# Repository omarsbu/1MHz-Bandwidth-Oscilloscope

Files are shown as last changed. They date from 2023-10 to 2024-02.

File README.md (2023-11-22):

# 1MHz-Bandwidth Mixed Signal Oscilloscope

- Created a cohesive mixed signal oscilloscope system integrating both hardware and software components.

- Designed a 50-ohm, 1MHz bandwidth analog front end with versatile signal processing capabilities
including, AC/DC coupled inputs, single-ended to differential signal conversion, SPI controlled variable gain
and attenuation, precise DC offset biasing, a 2nd order active anti-aliasing filter, and precise analog trigger
circuitry to interface with an 10 MSPS ADC.

- Developed Arduino C++ code for an ESP32 microcontroller to control an ILI9341 LCD display, enabling
real-time waveform plotting, XY cursors, frequency, period, duty cycle, and RMS measurements.
Implemented user-friendly controls via potentiometers and push buttons for vertical and horizontal scaling,
trigger level adjustment, and DC offset. Applied signal processing techniques for signal amplification,
attenuation, and dynamic upsampling and downsampling.

- A USB port outputs 5V of power so that an external microcontroller can be connected. The ADC output can also be read
  by an external microcontroller or FPGA. Header connectors can be used to read data from the analog front end and send
  control siignals to control signal conditioning.

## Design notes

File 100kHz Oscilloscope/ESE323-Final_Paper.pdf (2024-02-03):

Omar Mohamed

SBU ID - 113907357

ESE 323 – Modern Circuit Board Design and Prototyping

Final Paper

100KHz Bandwidth Oscilloscope

The goal of my project was to create a 100KHz bandwidth oscilloscope with control knobs for vertical

and horizontal scaling, dc offset addition/subtraction, trigger level adjustment, and XY measurement

cursors. I used Arduino IDE to write software in C++ for an ESP32 to plot the samples from the ADC on a

240x320 pixel TFT display, poll the control knobs, and perform tasks related to peripheral ICs. I designed

an analog front end for signal conditioning to maximize the ADC’s input range and triggering to plot a

stable waveform on an LCD display module. My goal is for oscilloscope to operate on a single +3.3V

power supply and be capable of receiving power from a USB connector or an AC adaptor. A block

diagram of my design is shown below:

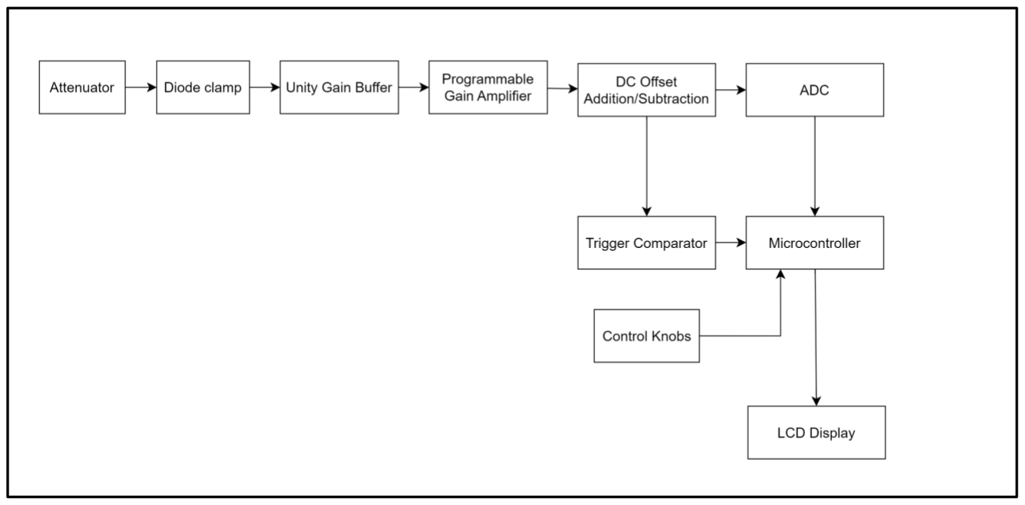
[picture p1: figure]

Circuit Description

Shown below is a schematic diagram of the input stage which consists of a pair of banana

connectors to connect external probes, a compensated L-pad attenuator with 1MΩ input

impedance, a diode clamp, and a unity gain buffer. A programmable gain amplifier is used as a

preamp to adjust the resolution and range of the analog-to-digital converter.

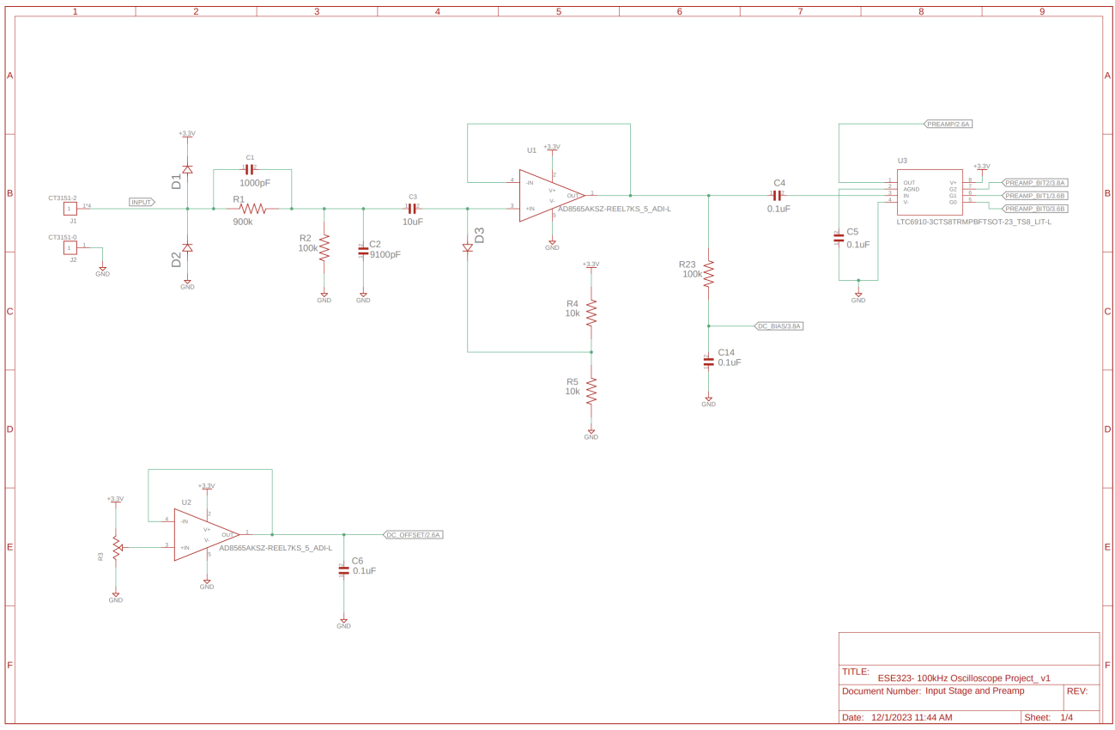
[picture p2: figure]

The Schottky diodes D1 and D2 are protection diodes which will forward bias and steer the flow of

current into the power supply if the input voltage is above or below the power supply rails.

Capacitors C1 and C2 are connected in parallel with resistors R1 and R2 to form a 10:1 L-pad attenuator.

The attenuator works in conjunction with the diode clamp to ensure that the input signal fits well within

the power supply rails so that signal distortion does not occur. If the input to the unity gain buffer is

outside of the range of the power-supply rails, then the signal will be clipped and there will be no way of

getting it to the ADC so it can be digitized. The positive clamp is used to shift the input signal up by the mid-supply voltage. This allows for negative input voltages to be measured with a single positive power

supply because it will automatically bias the input signal near the mid-supply voltage. The attenuator

helps to ensure that the input signal is small compared to the clamp voltage which increases the

likelihood of the input voltage level always being near the mid-supply voltage.

The trade-off of the clamp is that positive voltages above the mid-supply voltage will be shifted above

+3.3V and will be clipped while negative voltages above -1.65V will be shifted to within the single-supply

range. This is a good trade off to make since it allows for my oscilloscope to measure bipolar signals

which are of greater interest than signals with a single polarity. The positive input range can always be

increased by adding more attenuation to the input stage so there is less chance of being clipped.

The screenshot shown below is taken from an LTspice simulation of the analog front end:

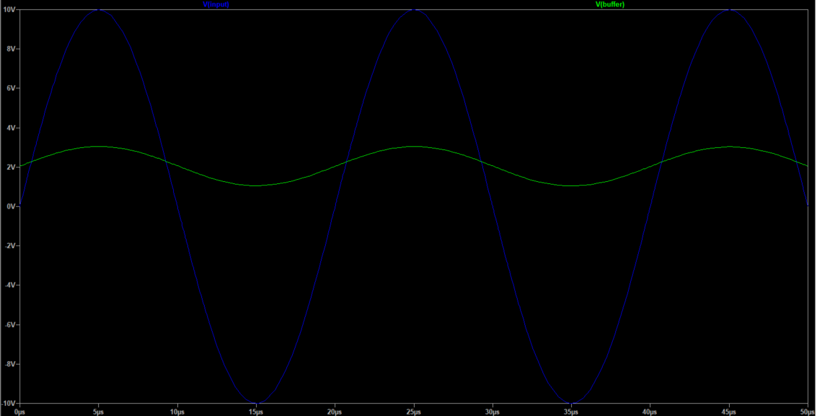
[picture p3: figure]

A 10V amplitude sine wave with 0 dc bias is applied at the input. The signal is attenuated and shifted up

to within the supply range of the op amp buffer so that even large negative voltages can still be

accommodated with a single positive power supply. Upon inspection, I forgot to account for the forward

voltage across the diode when clamping so the signal is shifted above the value I would like, however,

the values of resistors R4 and R5 can be adjusted to achieve a different clamp voltage.

Connecting capacitors C1 and C2 in parallel with resistor R1 and R2 provides compensation for the diode

clamp capacitance as well as the input capacitance of the amplifier and any stray capacitance or

inductance present in the resistors or circuit board. This compensation scheme employs pole-zero

cancellation to suppress undesirable frequency dependence caused by the additional reactance. If the

resistor and capacitor values are chosen so that the pole and the zero are superimposed, the transfer

function of the attenuator becomes independent of frequency. The component values are selected so

that the following relationship is satisfied:

R1C1 ≅ R2C2

The screenshot shown below is taken from an LTspice simulation of the attenuator output without compensation. The simulation shows that the desired 10:1 attenuation factor cannot be achieved without additional compensation.

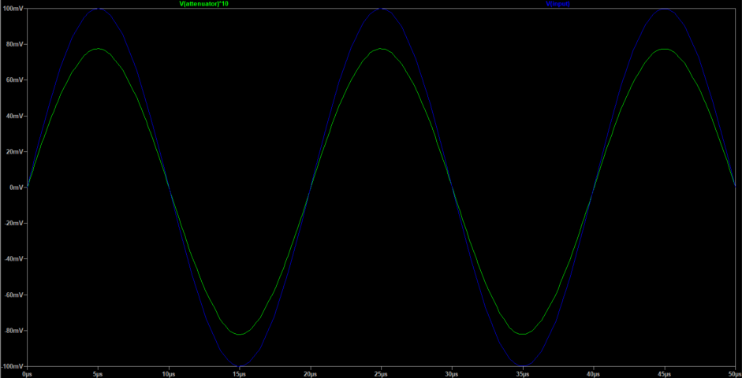
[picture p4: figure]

The screenshot shown below is taken from an LTspice simulation of the attenuator output with the appropriate compensation, the output is much closer to the desired 10:1 attenuation factor. The simulation results show that the attenuator performance is greatly improved by compensation.

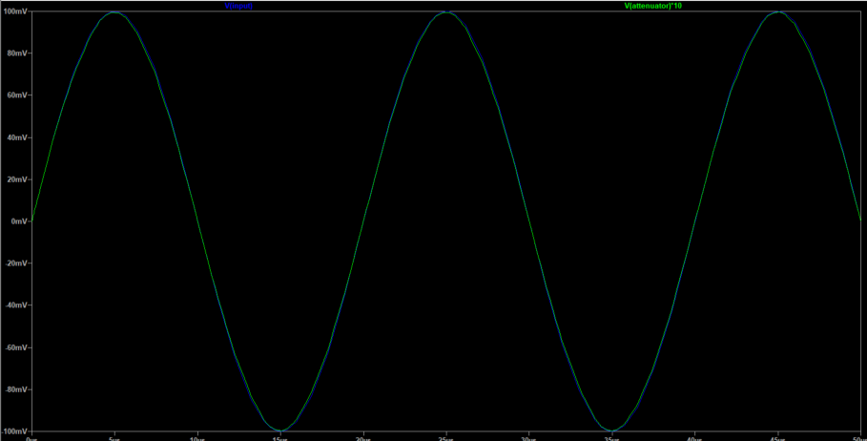
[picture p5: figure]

The programmable gain amplifier is used to provide variable amplification to the input signal so it can be

scaled to the ADC’s full range for maximum resolution. The gain of the amplifier is determined by the

volts per division setting on the oscilloscope. A lower volts per division setting would correspond to a

higher gain so that smaller signals can be scaled to the full range of the ADC and a higher volts per

division setting would correspond to a lower gain so that larger signals can still fit within the input range

of the ADC.

The LTC6910-2 is a 3-bit programmable gain amplifier with gain steps of 6dB (powers of 2). The gain of

the amplifier is cascaded with the attenuator so that variable gain and attenuation can be achieved. If

the gain of the amplifier is lower than the attenuation factor, then there will be a net attenuation of the

input and if the gain of the amplifier is higher than the attenuation factor then there will be a net

amplification of the input signal. The volts per division setting of the oscilloscope is implemented by

cascading the attenuator and PGA so the dynamic range of the ADC can be adjusted for more or less

effective resolution depending on the information being displayed on the screen.

The input signal is ac coupled to the amplifier so that only the ac portion of the signal is amplified.

Amplifying the dc component is of little use if it is larger than a few LSBs since it will mainly just shift the

input signal closer to the supply rails and introduce distortion or clipping. The signal is dc coupled to the

ADC of the ESP32 by measuring the voltage across a capacitor with a large RC time constant. If the time

constant of the capacitor is very large, then a low pass filter is formed to only allow dc to pass through.

The dc component of the input signal can then be measured with the ESP32’s ADC which is noisier and

has a lower sample rate than the external ADC being used. The noise and sample rate are less important

for the dc component than the ac component since it is just a vertical displacement of the ac component

on the display. An averaging filter can be implemented in software to remove any noise on the dc

measurement from the ESP32’s ADC.

DC offset addition or subtraction is implemented through the use of summing and differential op amp

configurations. The ADG1419 is a SPDT switch IC which is used to select between the outputs of the two

op amps. The dc offset select signal is a digital signal which is read from a push-button and set or cleared

by the microcontroller so that a dc offset can be added or subtracted from the amplified signal. The

output from the switch is connected to a comparator which compares the signal to the trigger level and

outputs a rising or falling edge when the signal passes through the trigger level. This edge triggers an

interrupt on the microcontroller which causes the waveform to be plotted on the screen. Since the

waveform is only plotted when the signal passes through the trigger level, a stable waveform can be

displayed on the screen.

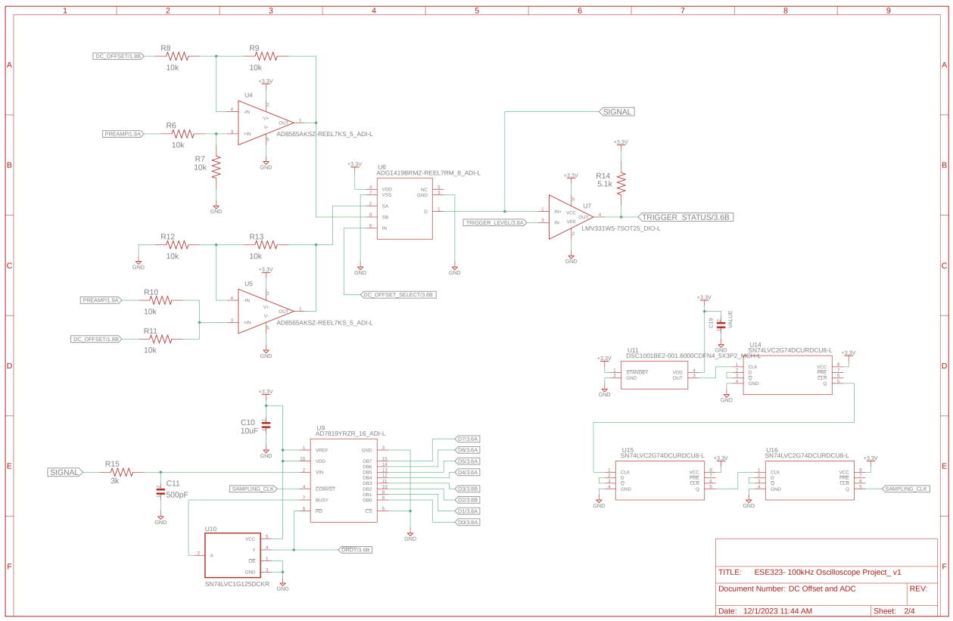
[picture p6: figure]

In hindsight, I now realize that the use of op amps for dc offsetting is a flaw in my design. The purpose of

dc offsetting is so that signals outside of the ADC’s input range can be shifted up or down to fit within the

appropriate input range. Since the reference voltage of the ADC is +3.3V which is the same as the power

supply voltage, using op amps for dc offsets does not do anything that cannot easily be done in software.

The op amps can only output voltages within its power supply rails which is no different from the ADC’s

input range, therefore, using op amps to shift the signal up or down does not provide any further

resolution to the ADC since the signal is already within its input range. Furthermore, the attenuator and

diode clamp at the input stage already perform the task of ensuring that the input signal is within the

ADC’s input range. Since the summing and differential op amps only serve to shift the signal up or down

within the ADC’s input range, they can be removed from the design and the same dc offsetting can be

implemented in software after the signal has been digitized.

The AD7819 is an 8-bit 200ksps SAR ADC, so a simple single-pole RC anti-aliasing filter is chosen with a

cutoff frequency close to the Nyquist-rate of 100kHz. A higher-order filter can be used to achieve a

steeper transition from the passband to stopband, however, this would require more components and

digital processing to flatten the passband response. I wanted to keep the design simple so that I could

finish as soon as possible. The RC-filter serves the purpose of preventing aliasing by filtering out

frequencies above the oscilloscope’s bandwidth, however, it also serves as a charge-bucket to reduce the

kickback settling time of the SAR ADC in between the conversion and acquisition phases by dumping

charge into the internal sample and hold circuit at the start of the acquisition phase.

The shortest possible time per division setting is proportional to the fastest sampling period (5

microseconds) multiplied by the number of samples displayed. In order to increase the time per division

setting on the display, a larger number of samples must be collected and then the sequence must be

decimated in order to display a waveform corresponding to the time per division setting. The ESP32 has

320KB of memory storage so there is enough memory to store a large number of 8-bit samples. The

sampling rate can be lowered to spread the samples over a longer time frame, however, this would

lower the oscilloscope’s bandwidth because I would have to ensure that the sampling rate was always

above the Nyquist rate.

A 200KHz sampling clock for the “conversion start” pin of the ADC is generated by using a 1.6MHz

oscillator and a D-flip-flop based frequency divider. Each stage divides the frequency by two, so three

flip-flops are cascaded to divide the frequency by eight and convert a 1.6MHz clock into a 200KHz clock.

A non-inverting buffer is used to increase the fanout of the BUSY pin as it must drive two input pins.

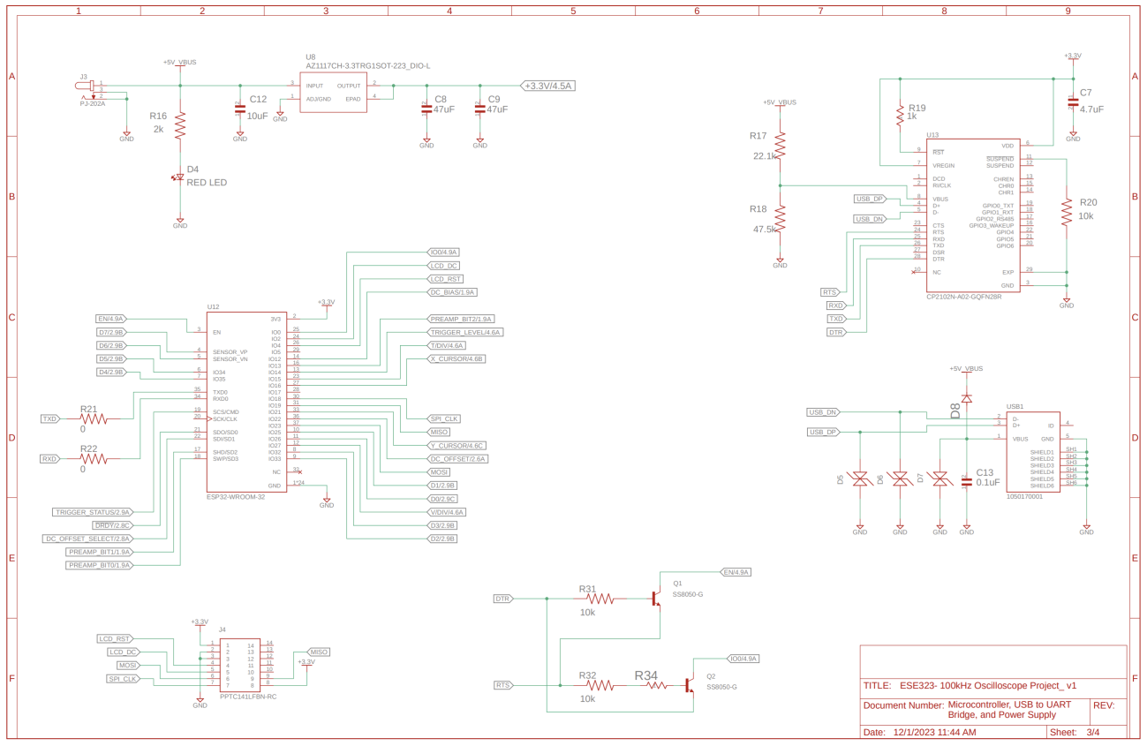
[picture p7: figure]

I have verified that I can sample all the GPIO pins connected to the ADC at a rate of 500kHz which is

more than twice the 200KHz frequency of the output from the ADC, therefore, no external FIFO buffer is

required to lower ADC’s output data rate. The microcontroller will poll the ADC output and store the

samples in memory and then plot the waveform on an LCD display after receiving the edge-triggered

interrupt from the trigger comparator.

A USB to UART bridge is used to program the microcontroller using Arduino IDE and a simple LDO

regulator is used to achieve the +3.3V power supply from a USB connector or a +5V ac adaptor. A red LED lights up when the power supply is connected to indicate that the board is receiving power. The ac

adaptor output and USB connector power pin are connected to the same node, however, a Schottky

diode is placed at the VBUS pin of the USB connector to prevent any current from flowing into the USB

host device. A 14-pin female header connector is used to mount an ILI9431 2.8” TFT LCD display on the

board.

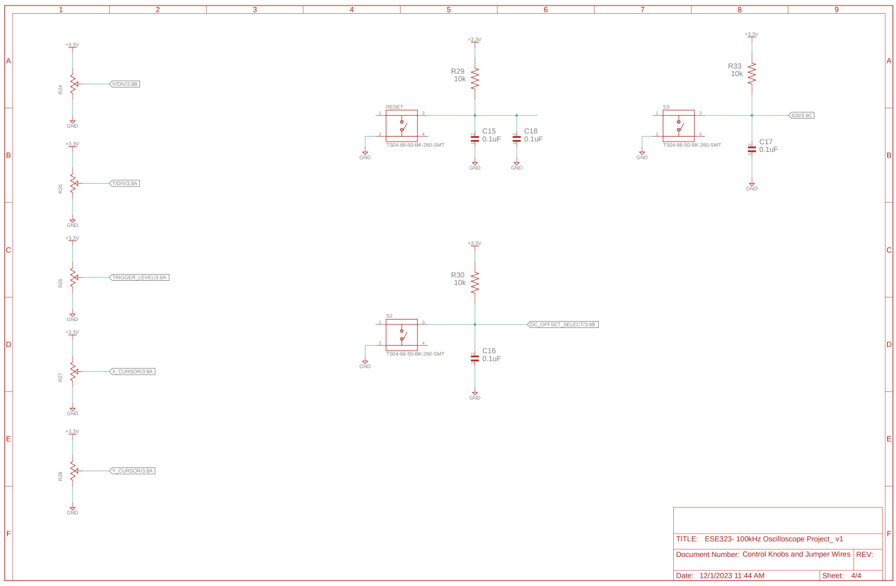
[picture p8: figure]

The control knobs are implemented using potentiometers. The output from the potentiometers

corresponding to the volts per division, time per division, and XY cursor settings are read by the ESP32’s

ADC and then software is used to map the analog values from the potentiometers onto the appropriate

horizontal/vertical scaling values and cursor positions on the screen. The PGA bits are chosen so

maximize resolution for a given volts per division setting and sample decimation is determined from the

time per division setting. The outputs from the trigger level and dc offset potentiometers are connected

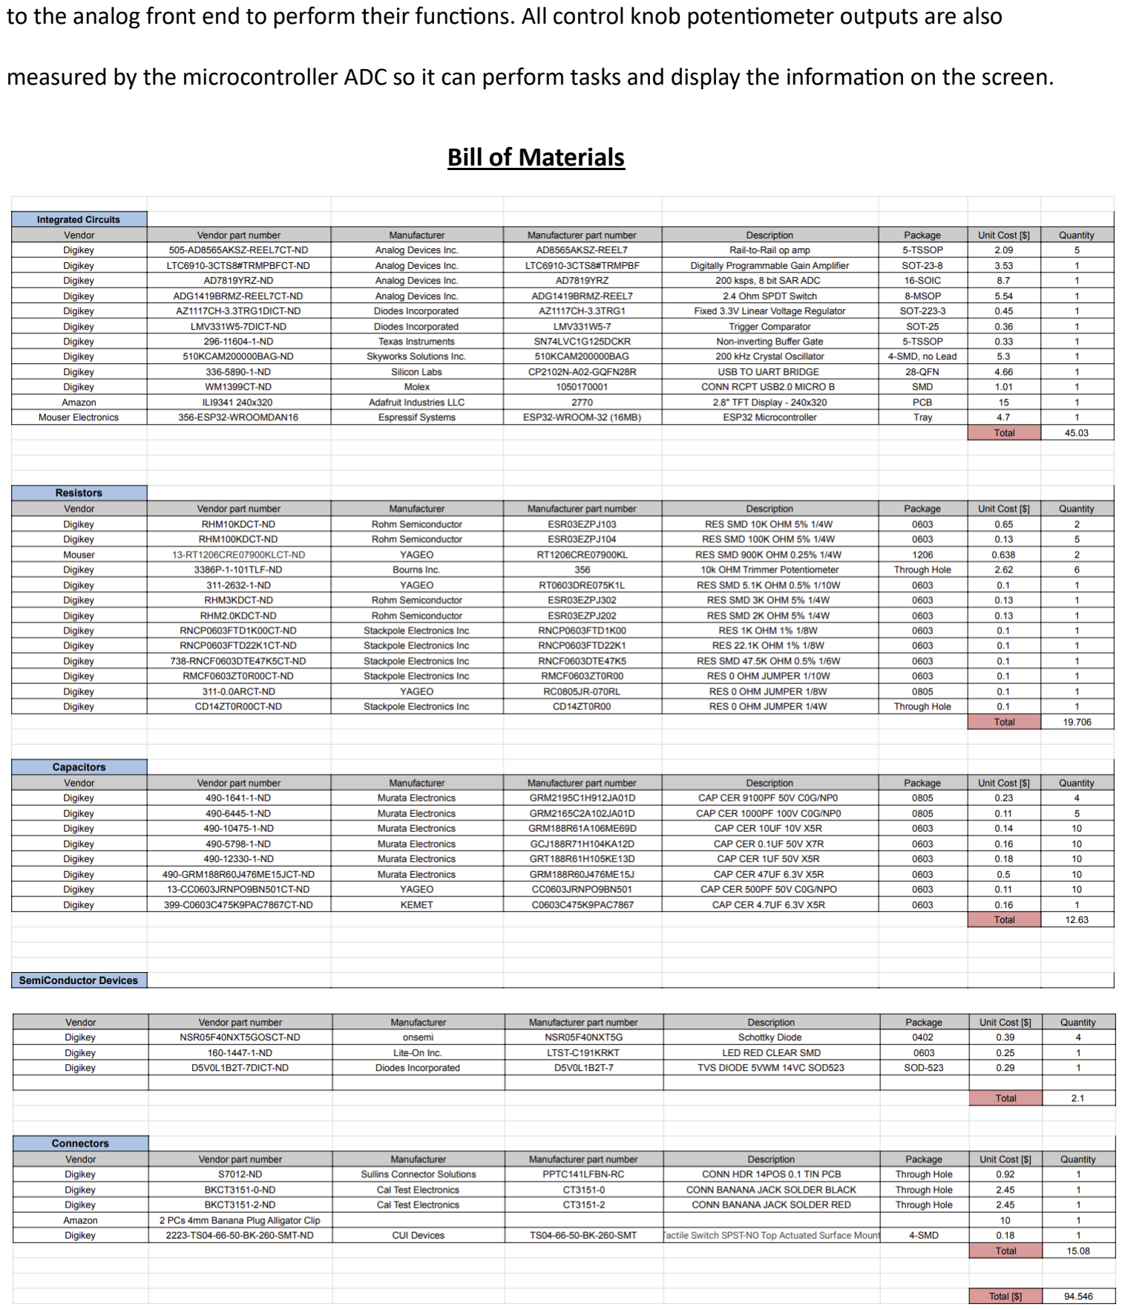
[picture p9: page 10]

to the analog front end to perform their functions. All control knob potentiometer outputs are also

measured by the microcontroller ADC so it can perform tasks and display the information on the screen.

Bill of Materials

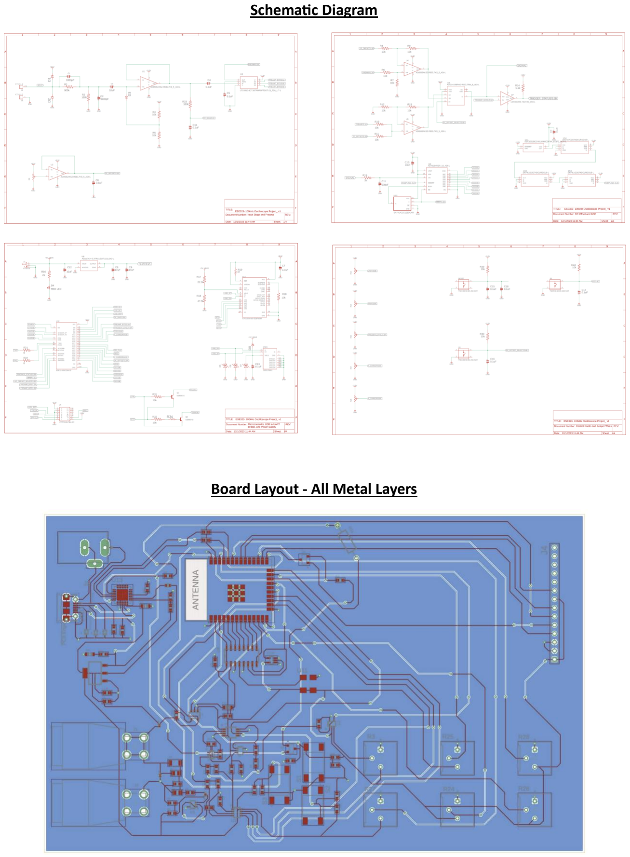
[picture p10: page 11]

Schematic Diagram

Board Layout - All Metal Layers

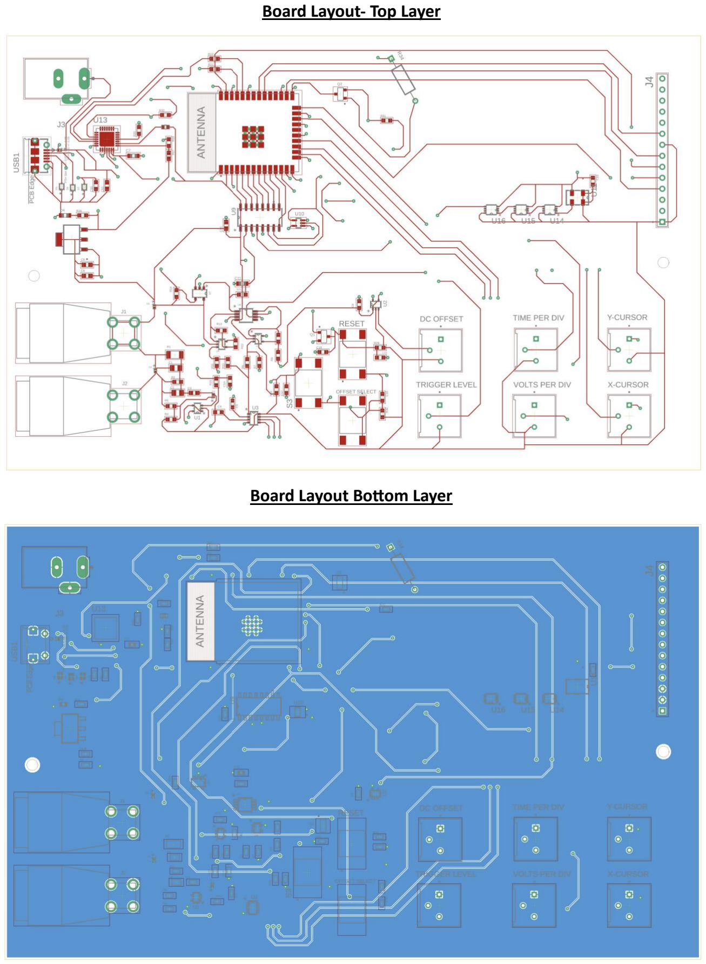
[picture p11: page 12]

Board Layout- Top Layer

Board Layout Bottom Layer

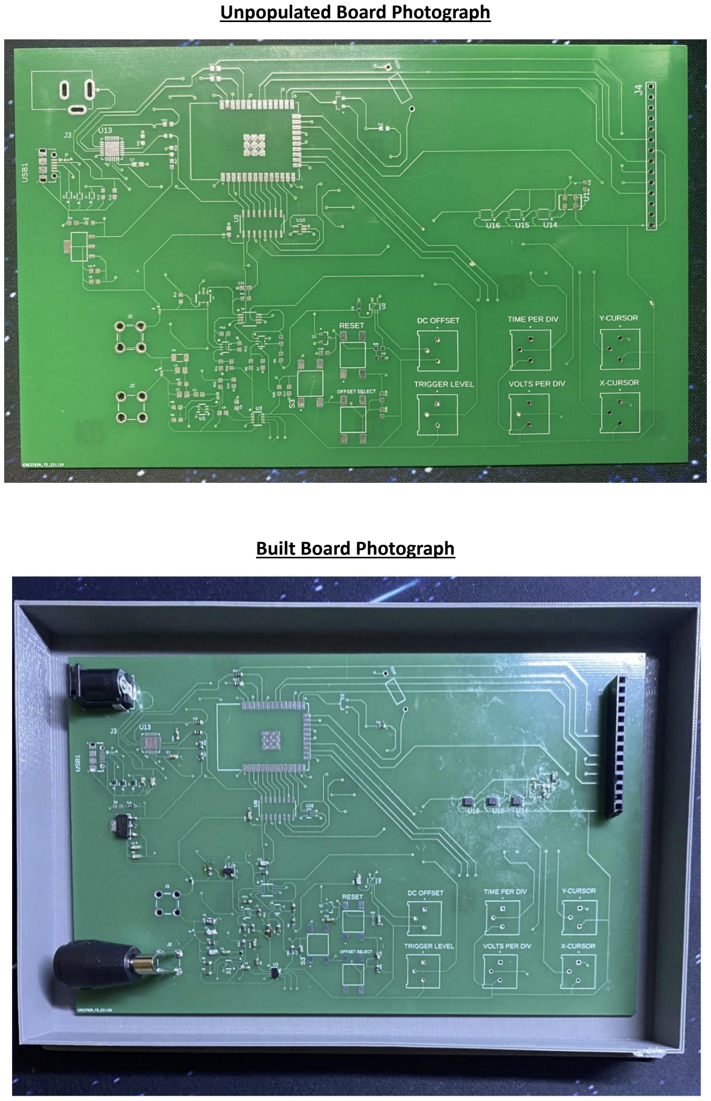
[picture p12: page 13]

Unpopulated Board Photograph

Built Board Photograph

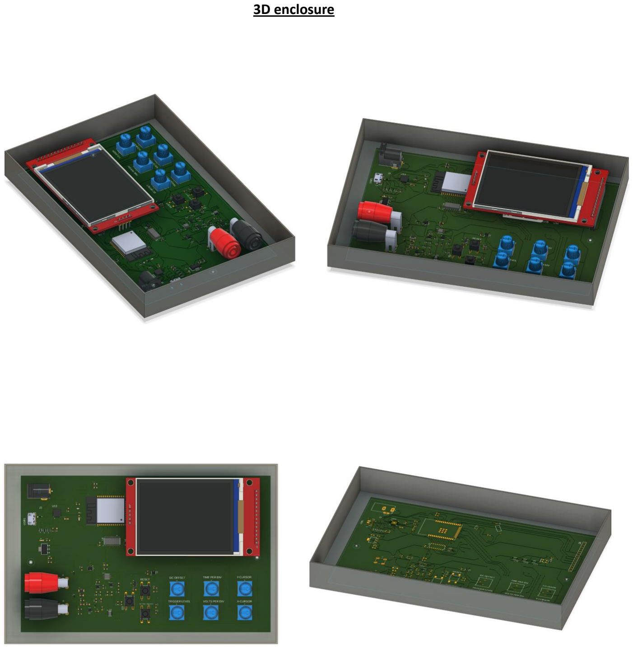
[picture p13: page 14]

3D enclosure

Software

This is a demonstration of the display code that I wrote for my project. I wanted to include a

photo of the code running on the actual display that I bought, however, I believe that I may have

left it in the lab over the weekend because I could not find it in my room. So instead, I used an

online Arduino simulator called Wokwi to simulate the code and I took a screenshot of the

results. The frequency , duty cycle, and period measurements are just arbitrary values that I

hardcoded onto the display. I tested the XY-cursors, volts per div, and time per div functions out

with my keyboard and the code worked how I wanted it to.

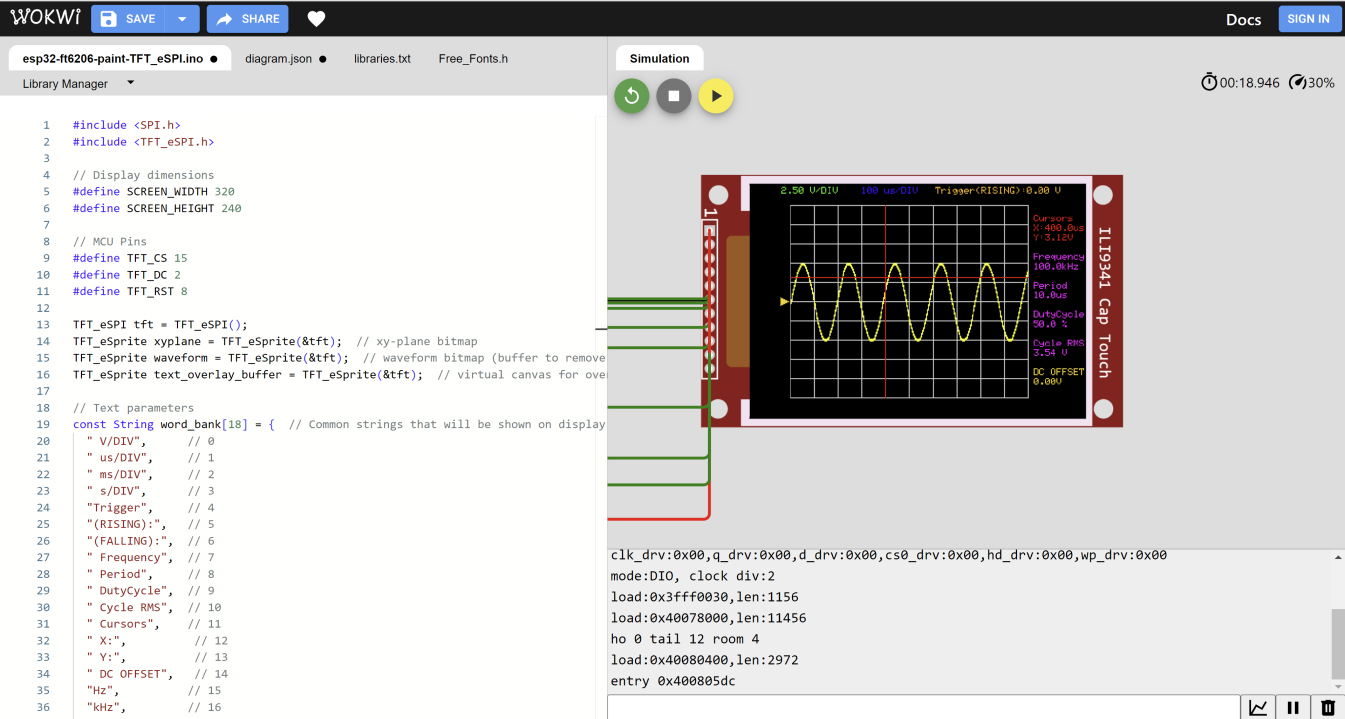
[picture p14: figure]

Results

My original design was too complicated to finish by the end of the semester, so I had to completely

redesign it from scratch over thanksgiving break. I was able to finish the layout and schematic,

unfortunately, I was not able to finish assembling my board. I lost most of my op amps and blew off

some of the pads for the board that I had made the most progress on. Also, the microcontroller that I

ordered from Digikey did not match the footprint that I found online so I could not solder it onto the

board. I decided not to solder on some of the more expensive components so I could save them for later.

I am going to order a new microcontroller that fits on the pad on my board, and I am also going to get

replacements for the components that I lost so I can try to assemble it next semester. I did get a chance

to test the programmable gain amplifier by soldering some of the gain bit pins to +3.3V. The two images

shown below are screenshots from one of the oscilloscopes in the lab. The green waveform (channel 2)

is the input signal, and the yellow waveform (channel 1) is the output from the amplifier.

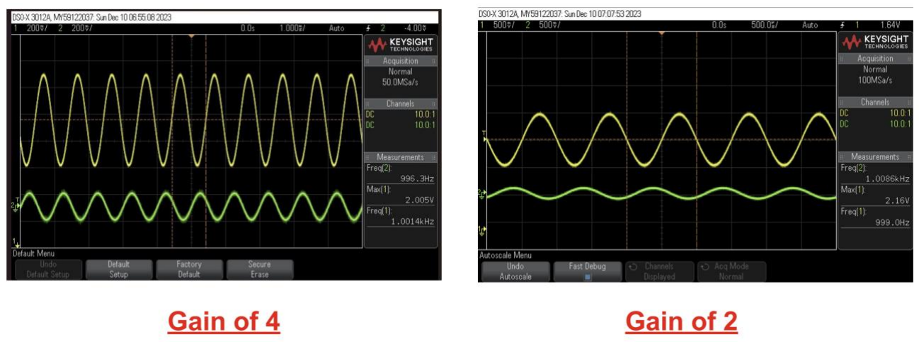
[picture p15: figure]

What would I do differently next time

Next time I will check the datasheets of my components to make sure that footprints from

online match the actual component that I am going to buy. I am also going to make a separate

board to practice soldering the packages that I buy to make sure that I do not make any

mistakes while assembling my board. I also would set a strict budget to make sure that I do not

overspend on parts. I am going to try and create a much more high-speed oscilloscope over the

winter and spring and that can get very expensive if I do not adhere to a strict budget.

Course Feedback

I think we should have started doing CAD work a lot earlier in the semester. I think if I had learned how

to do board layouts and 3D models in Fusion360 earlier, I would not have had to rush my project at the

end and I would have had a better chance to finish on time and double my footprints and packages. I

think we should have started learning how to do layouts and 3D models in September because the

“theoretical” information like trace properties and thermal resistance is a lot easier for me to in cram in

at the end of the semester than learning how to use CAD tools. That’s my personal opinion, I am not sure

if other people had a different experience than that.

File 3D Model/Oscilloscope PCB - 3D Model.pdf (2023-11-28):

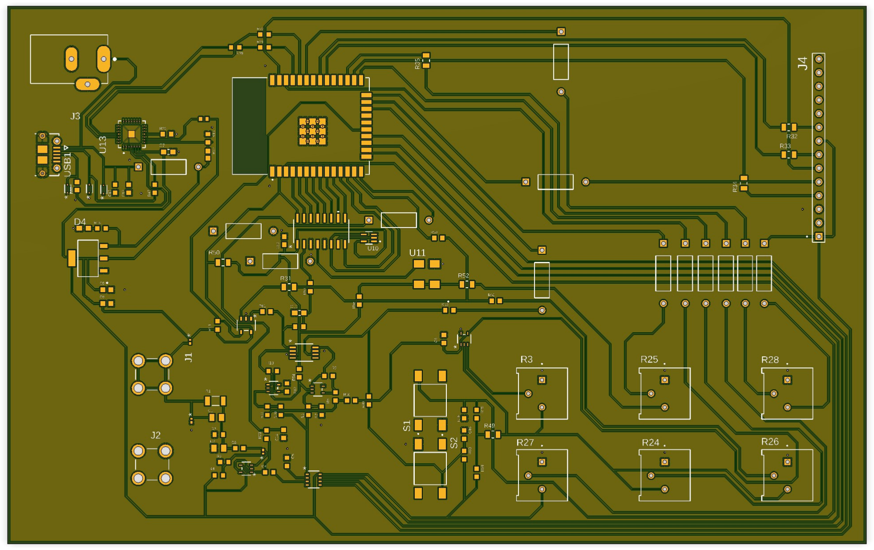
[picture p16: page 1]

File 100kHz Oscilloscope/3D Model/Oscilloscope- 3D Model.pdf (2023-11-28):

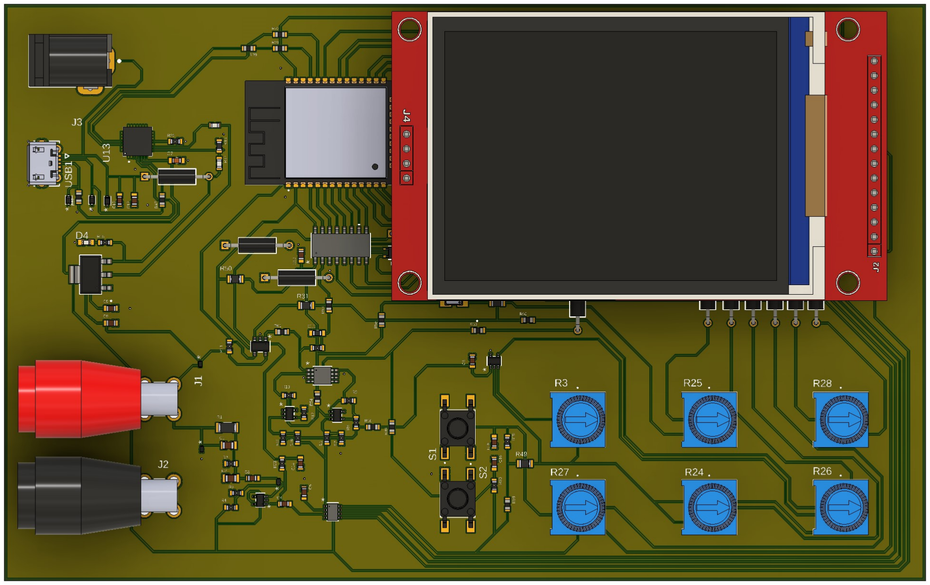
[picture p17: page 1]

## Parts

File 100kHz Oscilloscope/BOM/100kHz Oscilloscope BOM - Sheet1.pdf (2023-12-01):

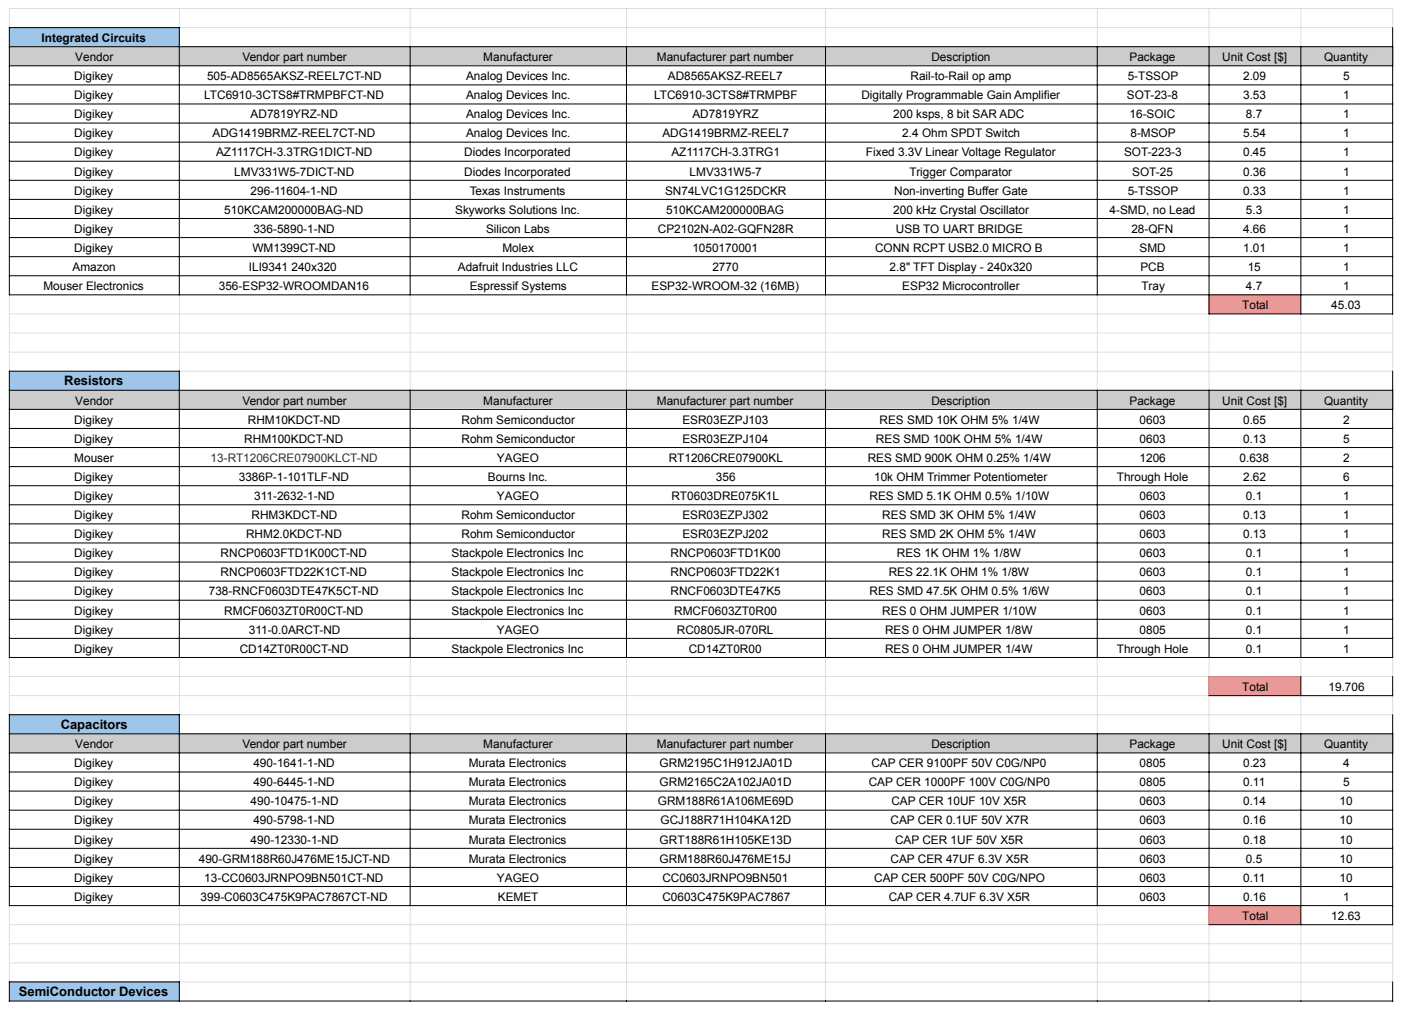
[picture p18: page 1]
Integrated Circuits; Resistors; Total; Capacitors; SemiConductor Devices

Vendor | Vendor part number | Manufacturer | Manufacturer part number | Description | Package | Unit Cost [$] | Quantity
Digikey | 505-AD8565AKSZ-REEL7CT-ND | Analog Devices Inc. | AD8565AKSZ-REEL7 | Rail-to-Rail op amp | 5-TSSOP | 2.09 | 5
Digikey | LTC6910-3CTS8#TRMPBFCT-ND | Analog Devices Inc. | LTC6910-3CTS8#TRMPBF | Digitally Programmable Gain Amplifier | SOT-23-8 | 3.53 | 1
Digikey | AD7819YRZ-ND | Analog Devices Inc. | AD7819YRZ | 200 ksps, 8 bit SAR ADC | 16-SOIC | 8.7 | 1
Digikey | ADG1419BRMZ-REEL7CT-ND | Analog Devices Inc. | ADG1419BRMZ-REEL7 | 2.4 Ohm SPDT Switch | 8-MSOP | 5.54 | 1
Digikey | AZ1117CH-3.3TRG1DICT-ND | Diodes Incorporated | AZ1117CH-3.3TRG1 | Fixed 3.3V Linear Voltage Regulator | SOT-223-3 | 0.45 | 1
Digikey | LMV331W5-7DICT-ND | Diodes Incorporated | LMV331W5-7 | Trigger Comparator | SOT-25 | 0.36 | 1
Digikey | 296-11604-1-ND | Texas Instruments | SN74LVC1G125DCKR | Non-inverting Buffer Gate | 5-TSSOP | 0.33 | 1
Digikey | 510KCAM200000BAG-ND | Skyworks Solutions Inc. | 510KCAM200000BAG | 200 kHz Crystal Oscillator | 4-SMD, no Lead | 5.3 | 1
Digikey | 336-5890-1-ND | Silicon Labs | CP2102N-A02-GQFN28R | USB TO UART BRIDGE | 28-QFN | 4.66 | 1
Digikey | WM1399CT-ND | Molex | 1050170001 | CONN RCPT USB2.0 MICRO B | SMD | 1.01 | 1
Amazon | ILI9341 240x320 | Adafruit Industries LLC | 2770 | 2.8" TFT Display - 240x320 | PCB | 15 | 1
Mouser Electronics | 356-ESP32-WROOMDAN16 | Espressif Systems | ESP32-WROOM-32 (16MB) | ESP32 Microcontroller | Tray | 4.7 | 1

Total | 45.03

Digikey | RHM10KDCT-ND | Rohm Semiconductor | ESR03EZPJ103 | RES SMD 10K OHM 5% 1/4W | 0603 | 0.65 | 2
Digikey | RHM100KDCT-ND | Rohm Semiconductor | ESR03EZPJ104 | RES SMD 100K OHM 5% 1/4W | 0603 | 0.13 | 5
Mouser | 13-RT1206CRE07900KLCT-ND | YAGEO | RT1206CRE07900KL | RES SMD 900K OHM 0.25% 1/4W | 1206 | 0.638 | 2
Digikey | 3386P-1-101TLF-ND | Bourns Inc. | 356 | 10k OHM Trimmer Potentiometer | Through Hole | 2.62 | 6
Digikey | 311-2632-1-ND | YAGEO | RT0603DRE075K1L | RES SMD 5.1K OHM 0.5% 1/10W | 0603 | 0.1 | 1
Digikey | RHM3KDCT-ND | Rohm Semiconductor | ESR03EZPJ302 | RES SMD 3K OHM 5% 1/4W | 0603 | 0.13 | 1
Digikey | RHM2.0KDCT-ND | Rohm Semiconductor | ESR03EZPJ202 | RES SMD 2K OHM 5% 1/4W | 0603 | 0.13 | 1
Digikey | RNCP0603FTD1K00CT-ND | Stackpole Electronics Inc | RNCP0603FTD1K00 | RES 1K OHM 1% 1/8W | 0603 | 0.1 | 1
Digikey | RNCP0603FTD22K1CT-ND | Stackpole Electronics Inc | RNCP0603FTD22K1 | RES 22.1K OHM 1% 1/8W | 0603 | 0.1 | 1
Digikey | 738-RNCF0603DTE47K5CT-ND | Stackpole Electronics Inc | RNCF0603DTE47K5 | RES SMD 47.5K OHM 0.5% 1/6W | 0603 | 0.1 | 1
Digikey | RMCF0603ZT0R00CT-ND | Stackpole Electronics Inc | RMCF0603ZT0R00 | RES 0 OHM JUMPER 1/10W | 0603 | 0.1 | 1
Digikey | 311-0.0ARCT-ND | YAGEO | RC0805JR-070RL | RES 0 OHM JUMPER 1/8W | 0805 | 0.1 | 1
Digikey | CD14ZT0R00CT-ND | Stackpole Electronics Inc | CD14ZT0R00 | RES 0 OHM JUMPER 1/4W | Through Hole | 0.1 | 1

Digikey | 490-1641-1-ND | Murata Electronics | GRM2195C1H912JA01D | CAP CER 9100PF 50V C0G/NP0 | 0805 | 0.23 | 4
Digikey | 490-6445-1-ND | Murata Electronics | GRM2165C2A102JA01D | CAP CER 1000PF 100V C0G/NP0 | 0805 | 0.11 | 5
Digikey | 490-10475-1-ND | Murata Electronics | GRM188R61A106ME69D | CAP CER 10UF 10V X5R | 0603 | 0.14 | 10
Digikey | 490-5798-1-ND | Murata Electronics | GCJ188R71H104KA12D | CAP CER 0.1UF 50V X7R | 0603 | 0.16 | 10
Digikey | 490-12330-1-ND | Murata Electronics | GRT188R61H105KE13D | CAP CER 1UF 50V X5R | 0603 | 0.18 | 10
Digikey | 490-GRM188R60J476ME15JCT-ND | Murata Electronics | GRM188R60J476ME15J | CAP CER 47UF 6.3V X5R | 0603 | 0.5 | 10
Digikey | 13-CC0603JRNPO9BN501CT-ND | YAGEO | CC0603JRNPO9BN501 | CAP CER 500PF 50V C0G/NPO | 0603 | 0.11 | 10
Digikey | 399-C0603C475K9PAC7867CT-ND | KEMET | C0603C475K9PAC7867 | CAP CER 4.7UF 6.3V X5R | 0603 | 0.16 | 1

Vendor | Vendor part number | Manufacturer | Manufacturer part number | Description | Package | Unit Cost [$] | Quantity
Digikey | NSR05F40NXT5GOSCT-ND | onsemi | NSR05F40NXT5G | Schottky Diode | 0402 | 0.39 | 4
Digikey | 160-1447-1-ND | Lite-On Inc. | LTST-C191KRKT | LED RED CLEAR SMD | 0603 | 0.25 | 1
Digikey | D5V0L1B2T-7DICT-ND | Diodes Incorporated | D5V0L1B2T-7 | TVS DIODE 5VWM 14VC SOD523 | SOD-523 | 0.29 | 1
Total | 2.1

Connectors

Vendor | Vendor part number | Manufacturer | Manufacturer part number | Description | Package | Unit Cost [$] | Quantity
Digikey | S7012-ND | Sullins Connector Solutions | PPTC141LFBN-RC | CONN HDR 14POS 0.1 TIN PCB | Through Hole | 0.92 | 1
Digikey | BKCT3151-0-ND | Cal Test Electronics | CT3151-0 | CONN BANANA JACK SOLDER BLACK | Through Hole | 2.45 | 1
Digikey | BKCT3151-2-ND | Cal Test Electronics | CT3151-2 | CONN BANANA JACK SOLDER RED | Through Hole | 2.45 | 1
Amazon | 2 PCs 4mm Banana Plug Alligator Clip | | | | | 10 | 1
Digikey | 2223-TS04-66-50-BK-260-SMT-ND | CUI Devices | TS04-66-50-BK-260-SMT | Tactile Switch SPST-NO Top Actuated Surface Mount | 4-SMD | 0.18 | 1
| | | | | | Total | 15.08
Total | 94.546

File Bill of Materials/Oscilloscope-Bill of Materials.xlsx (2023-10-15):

Integrated Circuits
Vendor | Vendor part number | Manufacturer | Manufacturer part number | Description | Package | Unit Cost [$] | Quantity
Digikey | 505-LTC1420CGN#PBF-ND | Analog Devices Inc. | LTC1420CGN#PBF | 10MSPS, 12-bit Piplined ADC | 28-SSOP | 15.67 | 1
Digikey | 505-AD8137YRZ-ND | Analog Devices Inc. | AD8137YRZ | Fully Differential ADC Driver | 8-SOIC | 3.75 | 2
Digikey | LTC6910-3CTS8#TRMPBFCT-ND | Analog Devices Inc. | LTC6910-3CTS8#TRMPBF | Digitally Programmable Gain Amplifier | SOT-23-8 | 3.53 | 4
Digikey | 110-CB3LV-3I-10M000000CT-ND | CTS-Frequency Controls | CB3LV-3I-10M000000 | 10 MHz Clock Oscillator | 4-SMD | 1.34 | 1
Digikey | 505-LTC6228IS6#TRMPBFCT-ND | Analog Devices Inc. | LTC6228IS6#TRMPBF | Rail-to-Rail Op Amp | SOT-23-6 | 5.62 | 1
Digikey | 505-LTC6752IS5#TRPBFCT-ND | Analog Devices Inc. | LTC6752IS5#TRPBF | Trigger Comparator | SOT-23-5 | 5.27 | 1
Digikey | AD8038ARZ-REEL7CT-ND | Analog Devices Inc. | AD8038ARZ-REEL7 | Voltage Feedback Amplifier | 8-SOIC | 2.92 | 1
Digikey | 296-33780-5-ND | Texas Instruments | SN74ALVC7804-40DL | 512 X 18 FIFO Memory Storage | 56-SSOP | 8.68 | 1
Amazon | ILI9341 240x320 | Adafruit Industries LLC | 2770 | 2.8" TFT Display - 240x320 | PCB | 15 | 1
Mouser Electronics | 356-ESP32-WROOMDAN16 | Espressif Systems | ESP32-WROOM-32 (16MB) | ESP32 Microcontroller | Tray | 4.7 | 1
Resistors
Vendor | Vendor part number | Manufacturer | Manufacturer part number | Description | Package | Unit Cost [$] | Quantity
Digikey | RNCP0603FTD1K00CT-ND | Stackpole Electronics Inc | RNCP0603FTD1K00 | 1k Ohm 1% 0.125W Thin film Resistor | 0603 | 0.1 | 6
Digikey | RNCP0603FTD4K02CT-ND | Stackpole Electronics Inc | RNCP0603FTD4K02 | 4k Ohm 1% 0.125W Thin Film Resistor | 0603 | 0.1 | 4
Digikey | 2019-RN73R1JTTD3161B25CT-ND | KOA Speer Electronics, Inc. | RN73R1JTTD3161B25 | 3.16k Ohm 0.1% 0.1W Thin Film Resistor | 0603 | 0.2 | 2
Digikey | 2019-RN73R1JTTD2001B25CT-ND | KOA Speer Electronics, Inc. | RN73R1JTTD2001B25 | 2k Ohm 0.1% 0.1W Thin Film Resistor | 0603 | 0.2 | 4
Digikey | P1.33KDBCT-ND | Panasonic Electronic Components | ERA-3AEB1331V | 1.33k Ohm 0.1% 0.1W Thin Film Resistor | 0603 | 0.31 | 2
Digikey | 2019-RN73R1JTTD1052B25CT-ND | KOA Speer Electronics, Inc. | RN73R1JTTD1052B25 | 10.5k Ohm 0.1% 0.1W Thin Film Resistor | 0603 | 0.2 | 4
Digikey | P6.04KDBCT-ND | Panasonic Electronic Components | ERA-3AEB6041V | 6.04k Ohm 0.1% 0.1W Thin Film Resistor | 0603 | 0.31 | 2
Digikey | 2019-RN73R1JTTD49R9B25CT-ND | KOA Speer Electronics, Inc. | RN73R1JTTD49R9B25 | 49.9 Ohm 0.1% 0.1W Thin Film Resistor | 0603 | 0.2 | 7
Digikey | P348DBCT-ND | Panasonic Electronic Components | ERA-3AEB3480V | 348 Ohm 0.1% 0.1W Thin Film Resistor | 0603 | 0.31 | 1
Digikey | P150DBCT-ND | Panasonic Electronic Components | ERA-3AEB151V | 150 Ohm 0.1% 0.1W Thin Film Resistor | 0603 | 0.31 | 1
Digikey | 2019-RN73R1JTTD1000B25CT-ND | KOA Speer Electronics, Inc. | RN73R1JTTD1000B25 | 100 Ohm 0.1% 0.1W Thin Film Resistor | 0603 | 0.2 | 1
Digikey | 2019-RN73R1JTTD2000B25CT-ND | KOA Speer Electronics, Inc. | RN73R1JTTD2000B25 | 200 Ohm 0.1% 0.1W Thin Film Resistor | 0603 | 0.2 | 1
Capacitors
Vendor | Vendor part number | Manufacturer | Manufacturer part number | Description | Package | Unit Cost [$] | Quantity
Digikey | 445-7344-1-ND | TDK Corporation | C1005X7R1V104K050BB | 0.1uF 10% 35V Ceramic Capacitor | 0402 | 0.1 | 3
Digikey | 399-C0402C105K9PAC7867CT-ND | KEMET | C0402C105K9PAC7867 | 1uF 10% 6.3V Ceramic Capacitor | 0402 | 0.1 | 4
Digikey | 311-1424-1-ND | YAGEO | CC0603JRNPO9BN200 | 20pF 5% 50V Ceramic Capacitor | 0603 | 0.1 | 1
Digikey | 311-1058-1-ND | YAGEO | CC0603JRNPO9BN100 | 10pF 5% 50V Ceramic Capacitor | 0603 | 0.1 | 2
Digikey | 13-CC0603JRNPO9BN501CT-ND | YAGEO | CC0603JRNPO9BN501 | 500pF 5% 50V Ceraamic Capacitor | 0603 | 0.11 | 1
Digikey | 311-1061-1-ND | YAGEO | CC0603JRNPO9BN180 | 18pF 5% 50V Ceramic Capacitor | 0603 | 0.1 | 2
Digikey | 311-1069-1-ND | YAGEO | CC0603JRNPO9BN101 | 100pF 5% 50V Ceramic Capacitor | 0603 | 0.1 | 1
Switches
Vendor | Vendor part number | Manufacturer | Manufacturer part number | Description | Package | Unit Cost [$] | Quantity
Digikey | 255-1355-5-ND | Panasonic Electric Works | TQ2-L2-9V | 1A 9V DPDT Latching Dual Coil Relay | Through Hole | 3.66 | 2
Digikey | 2223-TS02-66-60-BK-100-SCR-D-ND | CUI Devices | TS02-66-60-BK-100-SCR-D | SPST Tactile Pushbutton Switch | Through Hole | 0.1 | 10
Digikey | 3386P-1-101TLF-ND | Bourns Inc. | 356 | 10k Ohm Trimmer Potentiometer | Through Hole | 2.62 | 1
Semiconductor Devices
Vendor | Vendor part number | Manufacturer | Manufacturer part number | Description | Package | Unit Cost [$] | Quantity
Digikey | NSR05F40NXT5GOSCT-ND | onsemi | NSR05F40NXT5G | Schottky Diode | 0402 | 0.39 | 4
Digikey | 2N7002-FDICT-ND | Diodes Incorporated | 2N7002-7-F | 60V 115mA n-channel MOSFET | SOT-23-3 | 0.2 | 2

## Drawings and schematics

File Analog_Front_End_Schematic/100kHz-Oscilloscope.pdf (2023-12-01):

A

A

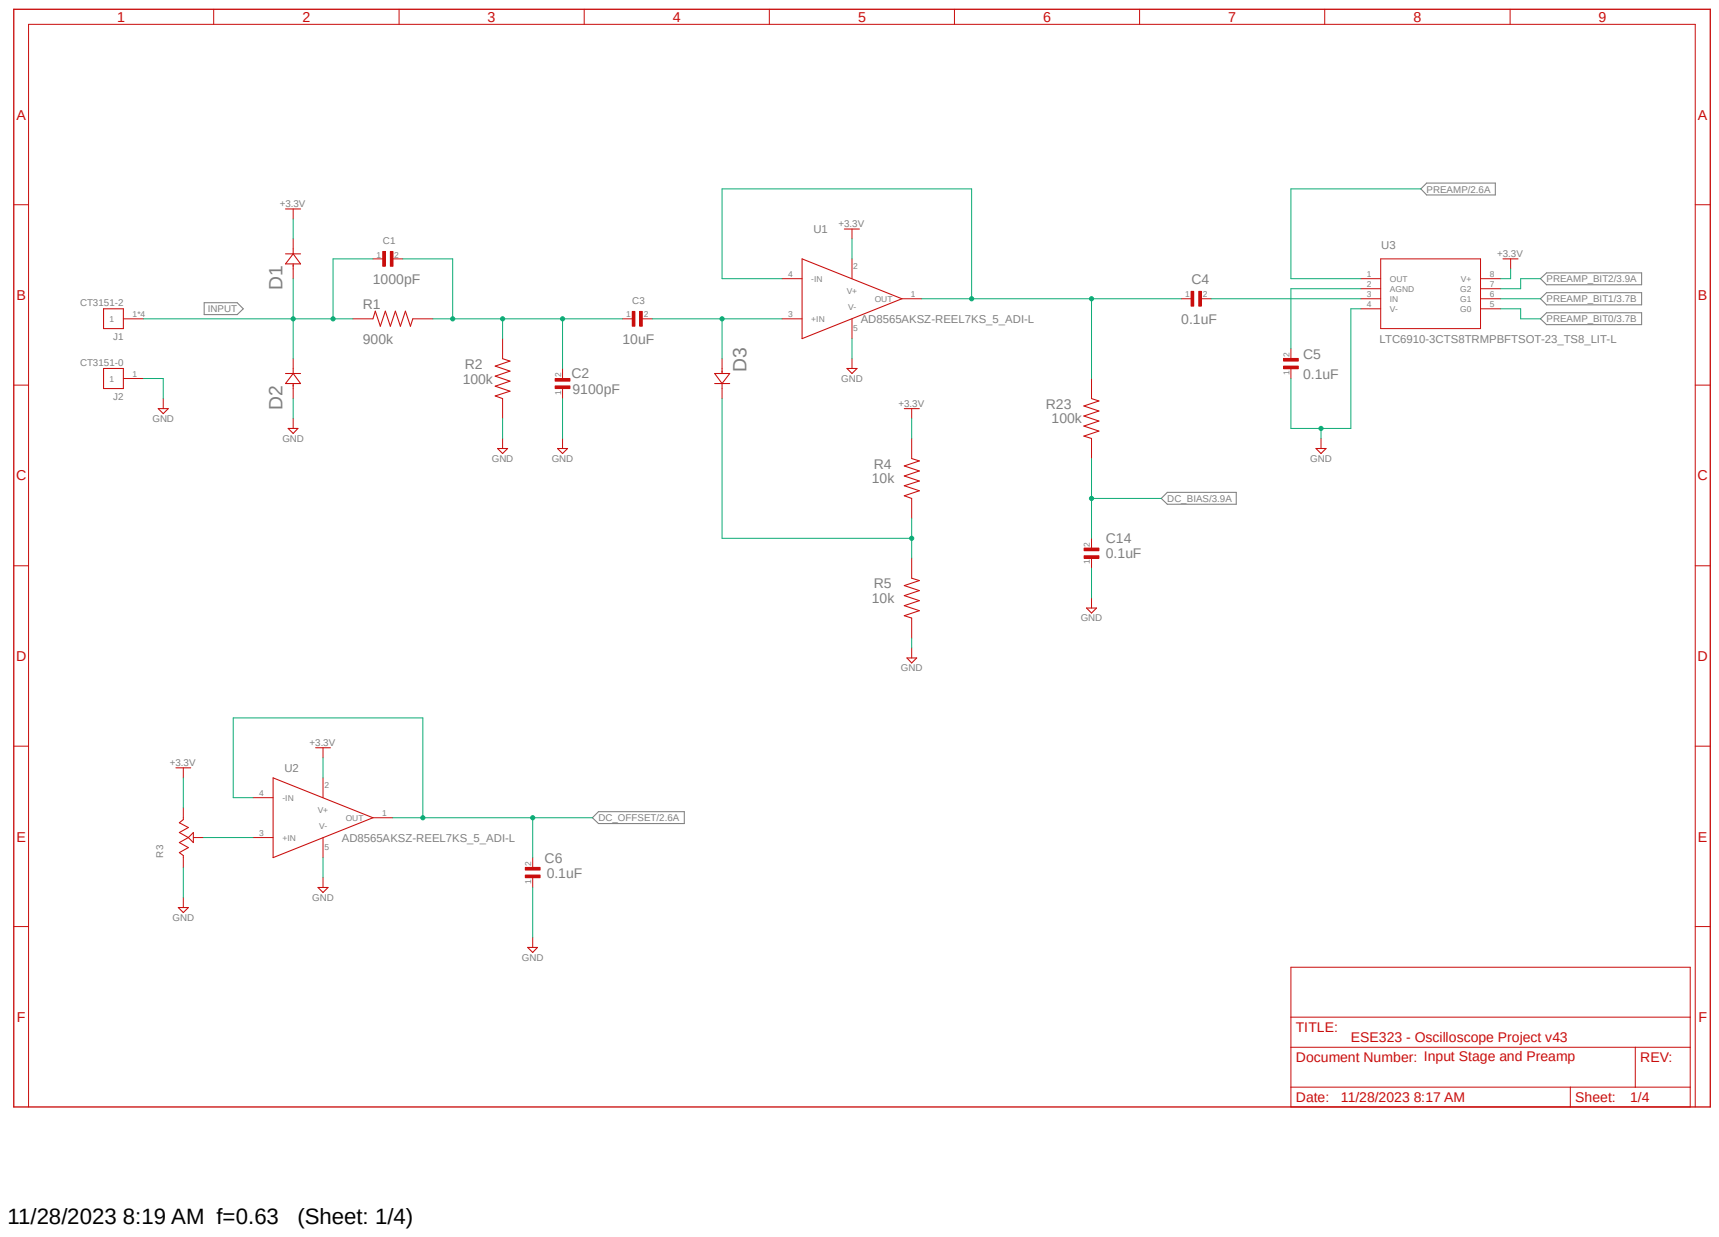
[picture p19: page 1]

Date: Sheet: Input Stage and Preamp | REV: TITLE: Document Number:

10k | 10k

# +3.3V GND

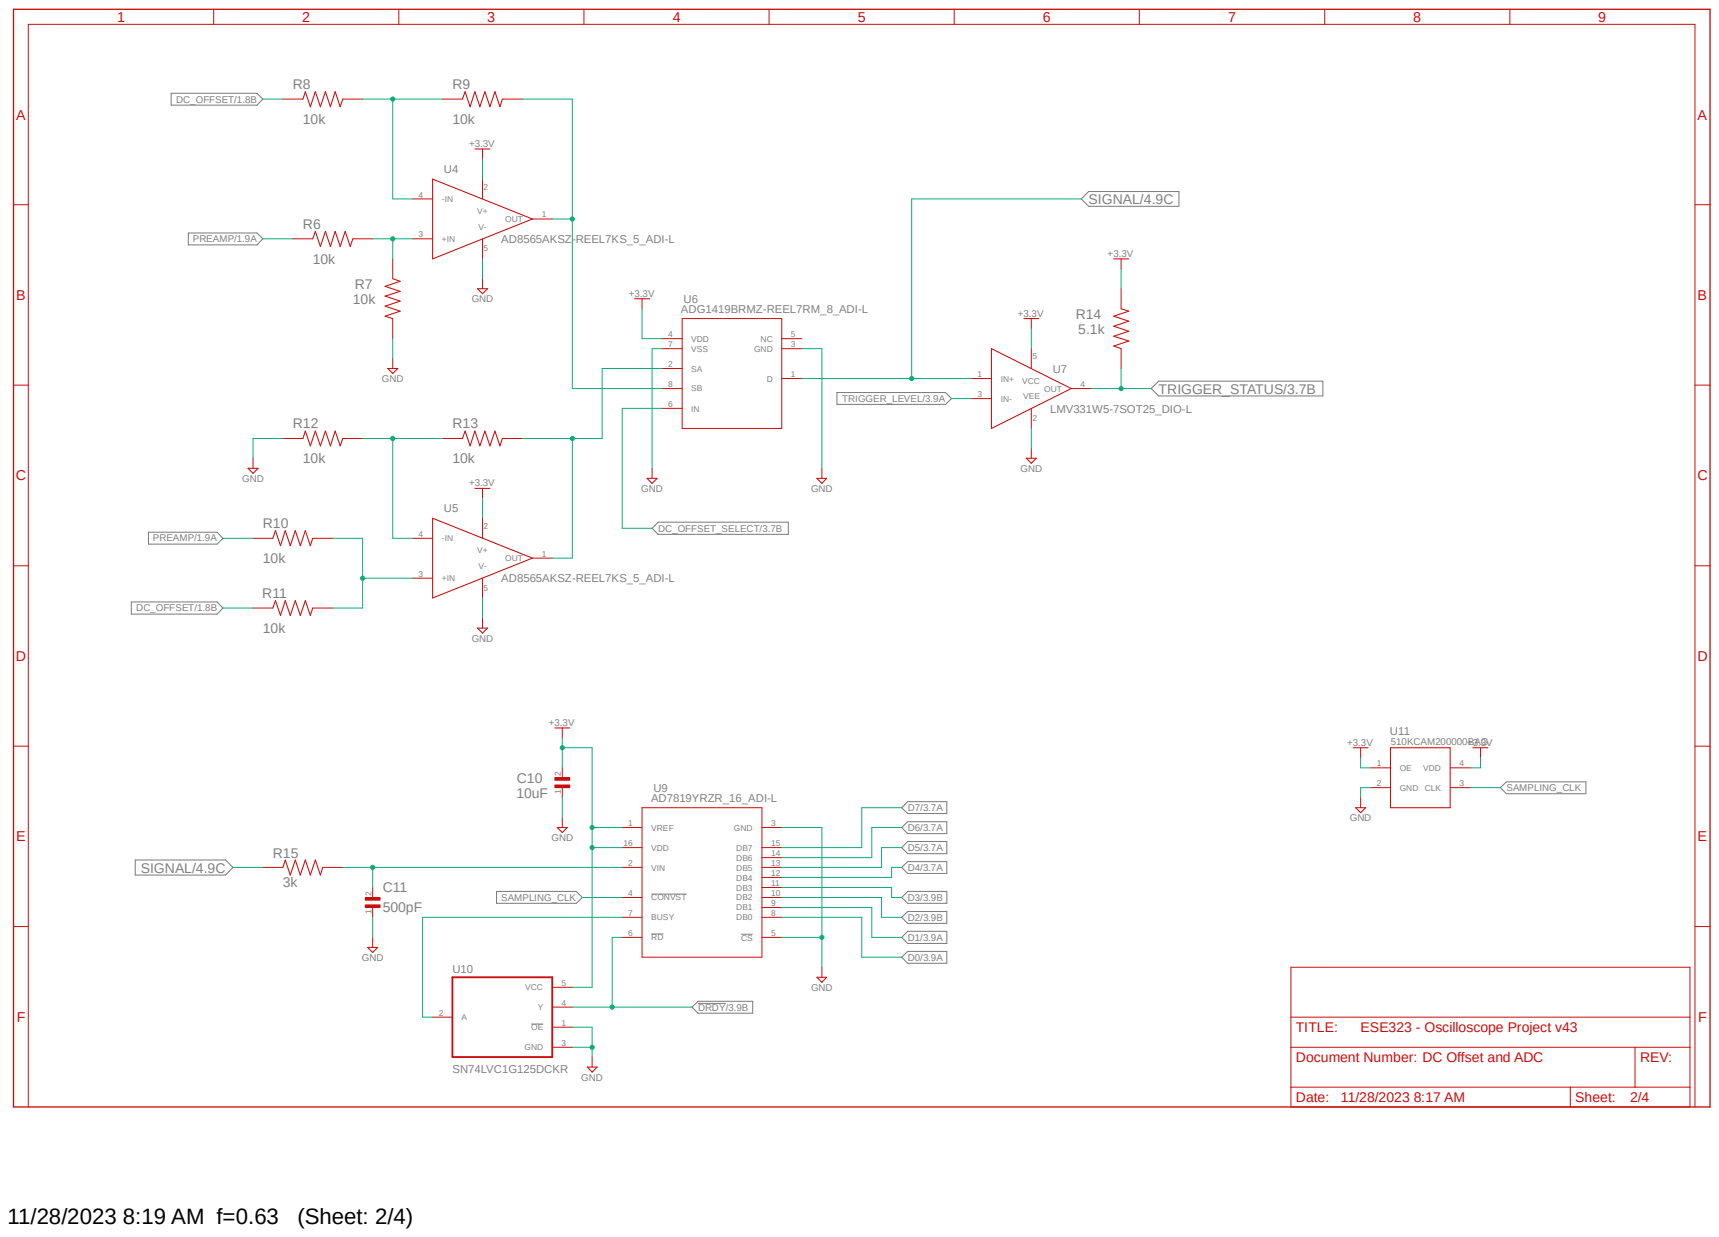
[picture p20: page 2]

Date: Sheet: DC Offset and ADC | REV: TITLE: Document Number:

1k

# 10k 4.7uF

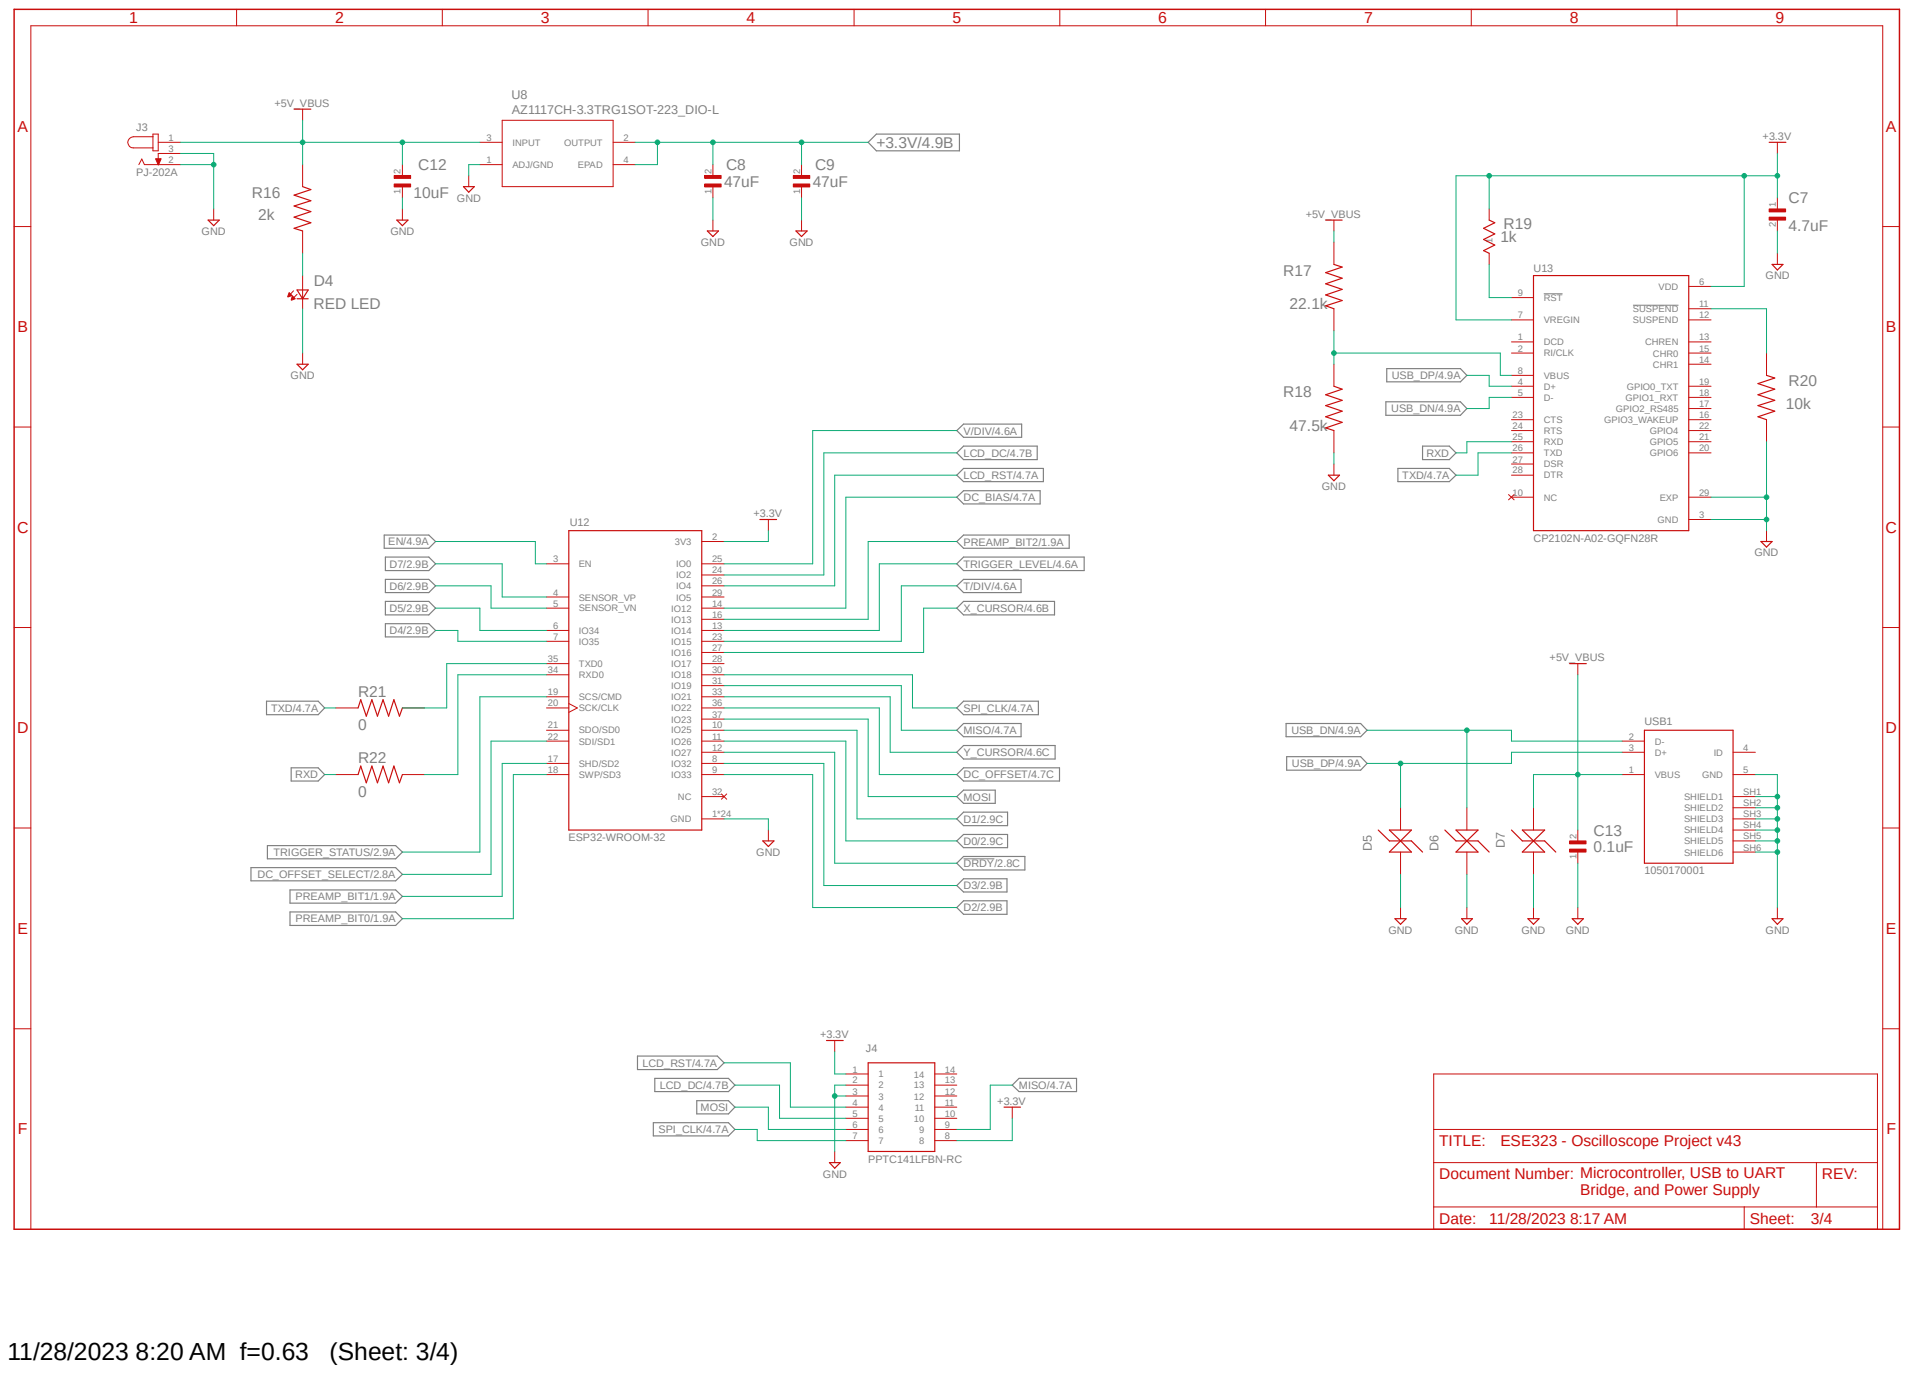
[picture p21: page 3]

D1/2.9C MISO/4.7A MISO/4.7A MOSI MOSI

5 | 10 10

Bridge, and Power Supply

10k

0

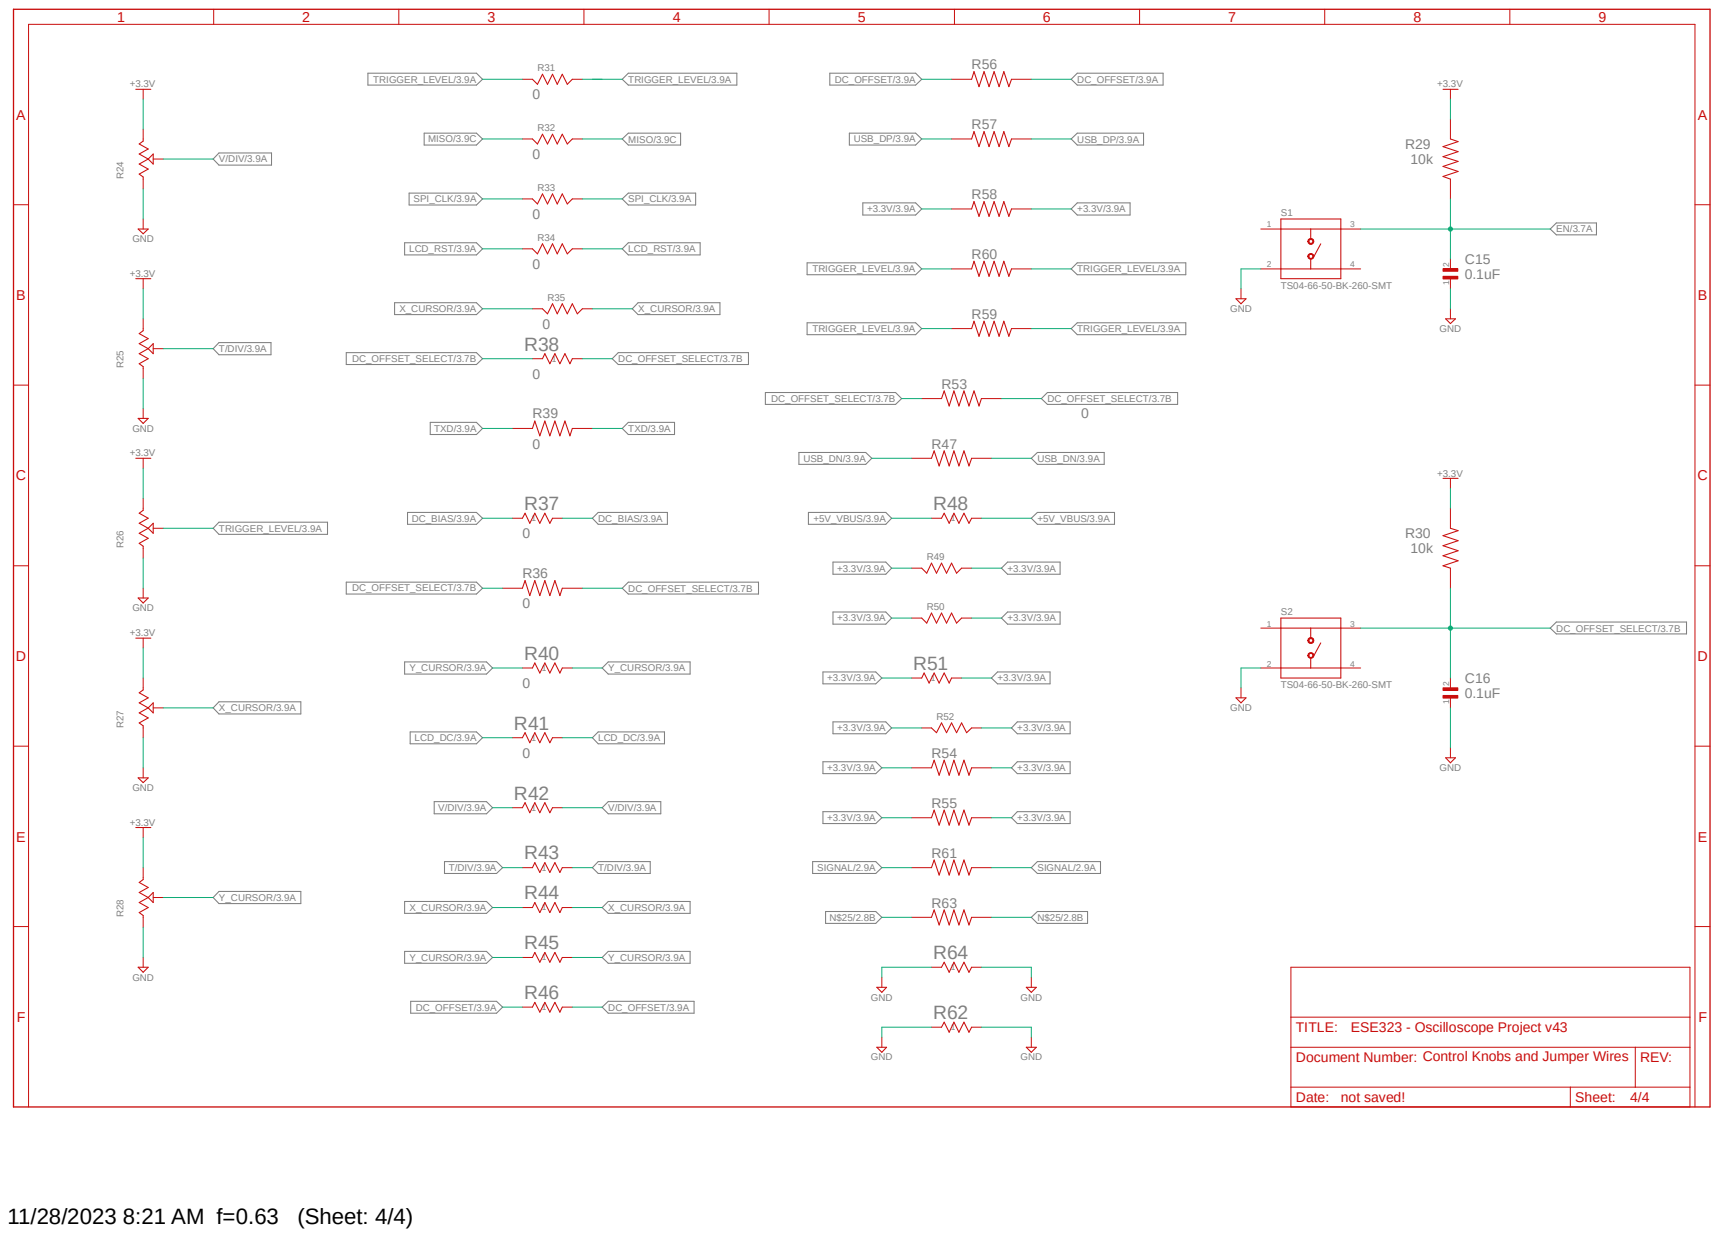
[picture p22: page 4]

Date: Sheet: | REV: TITLE: Document Number:

not saved! | 4/4

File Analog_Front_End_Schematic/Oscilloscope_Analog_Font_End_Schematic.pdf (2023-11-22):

## 2N7002-7-FSOT-23_1_DIO

## D3 U11 G

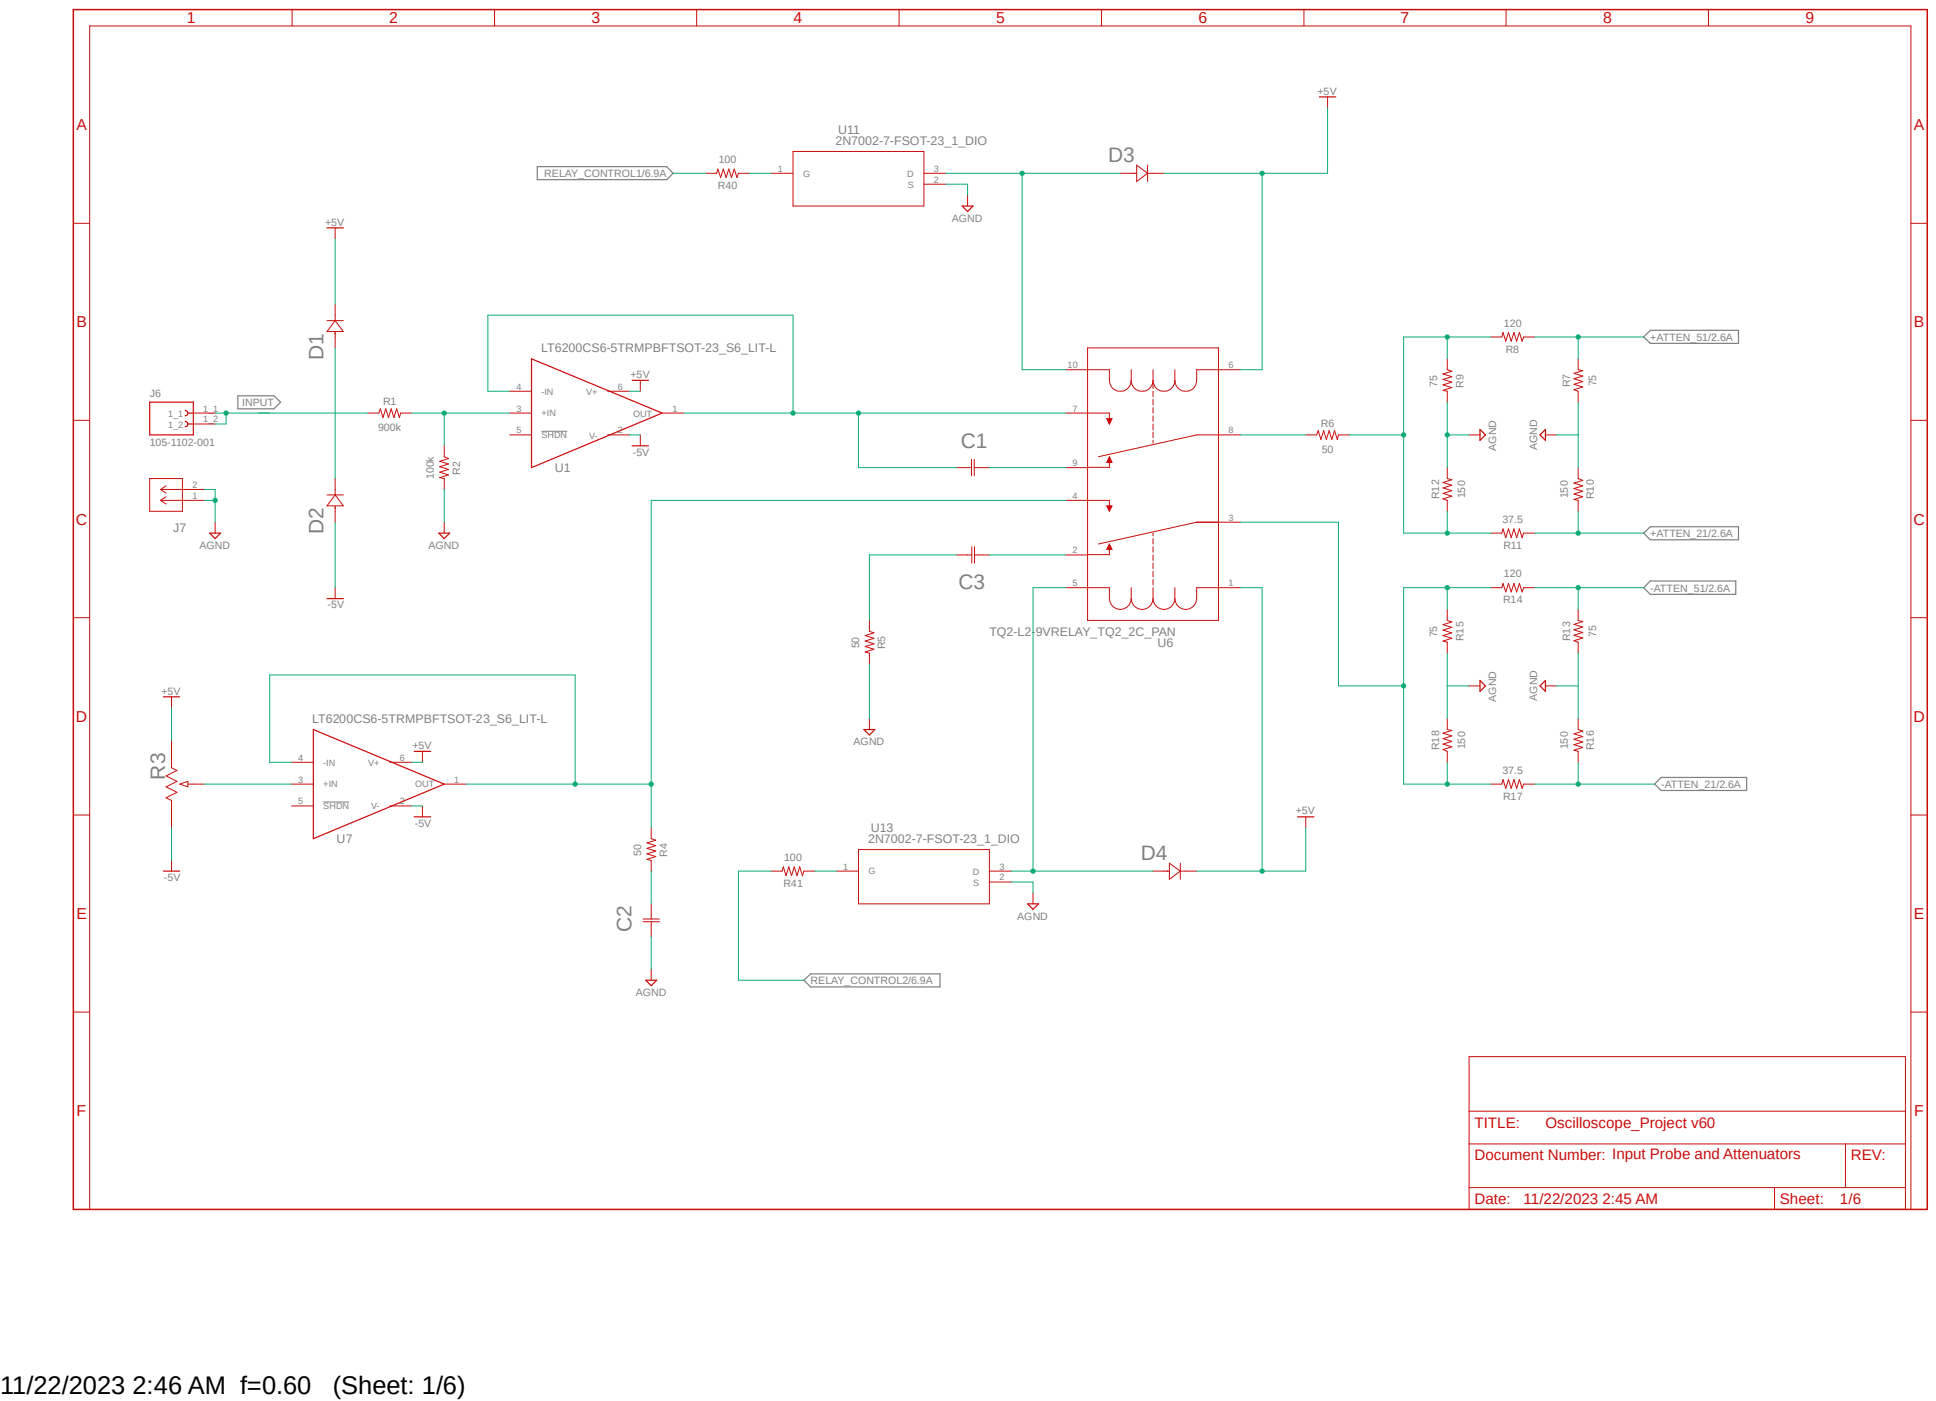
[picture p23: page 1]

Input Probe and Attenuators

## 2N7002-7-FSOT-23_1_DIO

C6

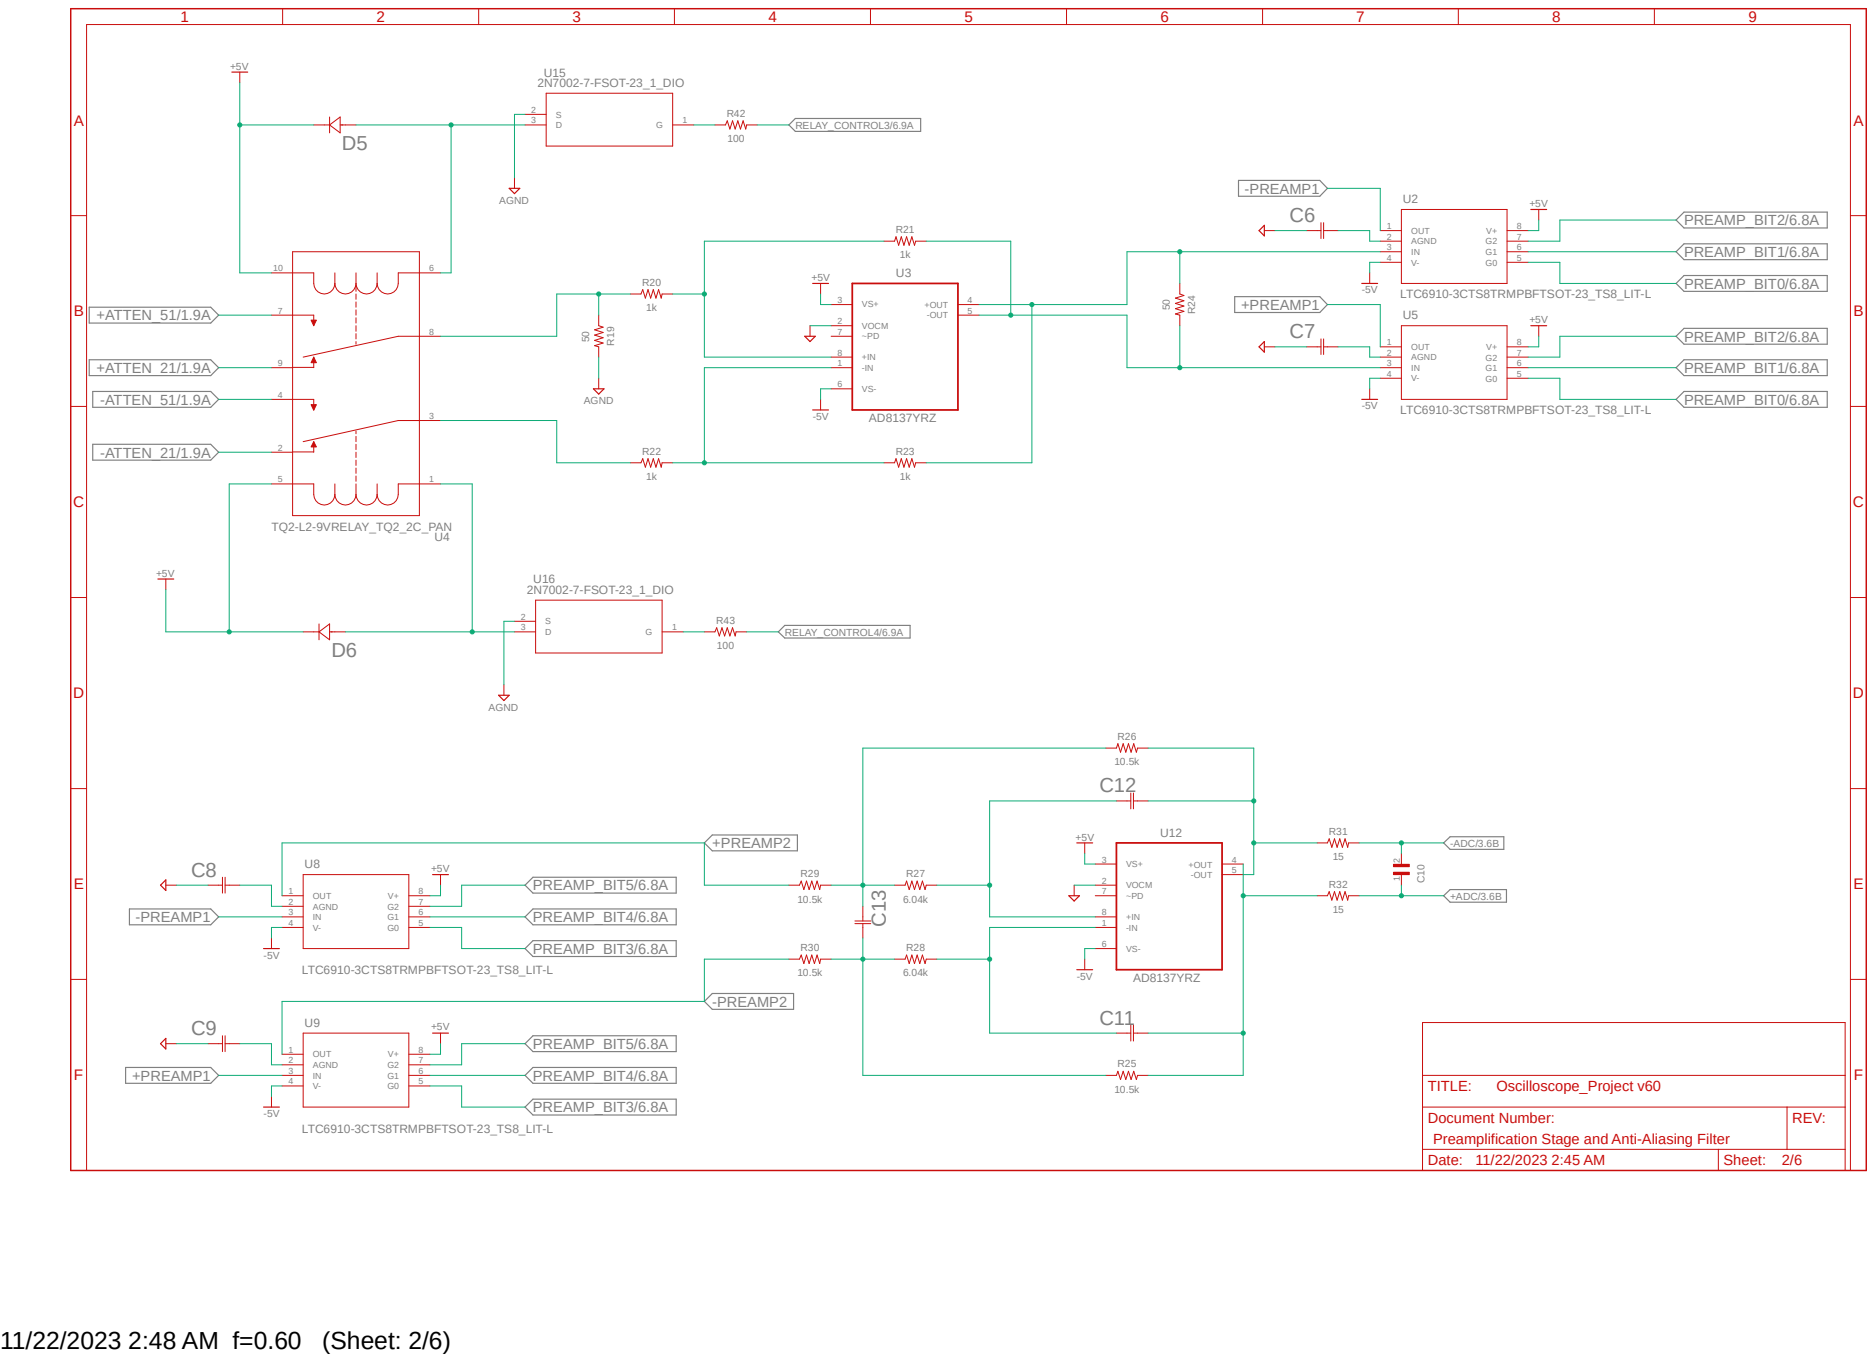
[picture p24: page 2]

Preamplification Stage and Anti-Aliasing Filter

## LTC1420CGNPBFSSOP-28_GN_LIT-L

C4

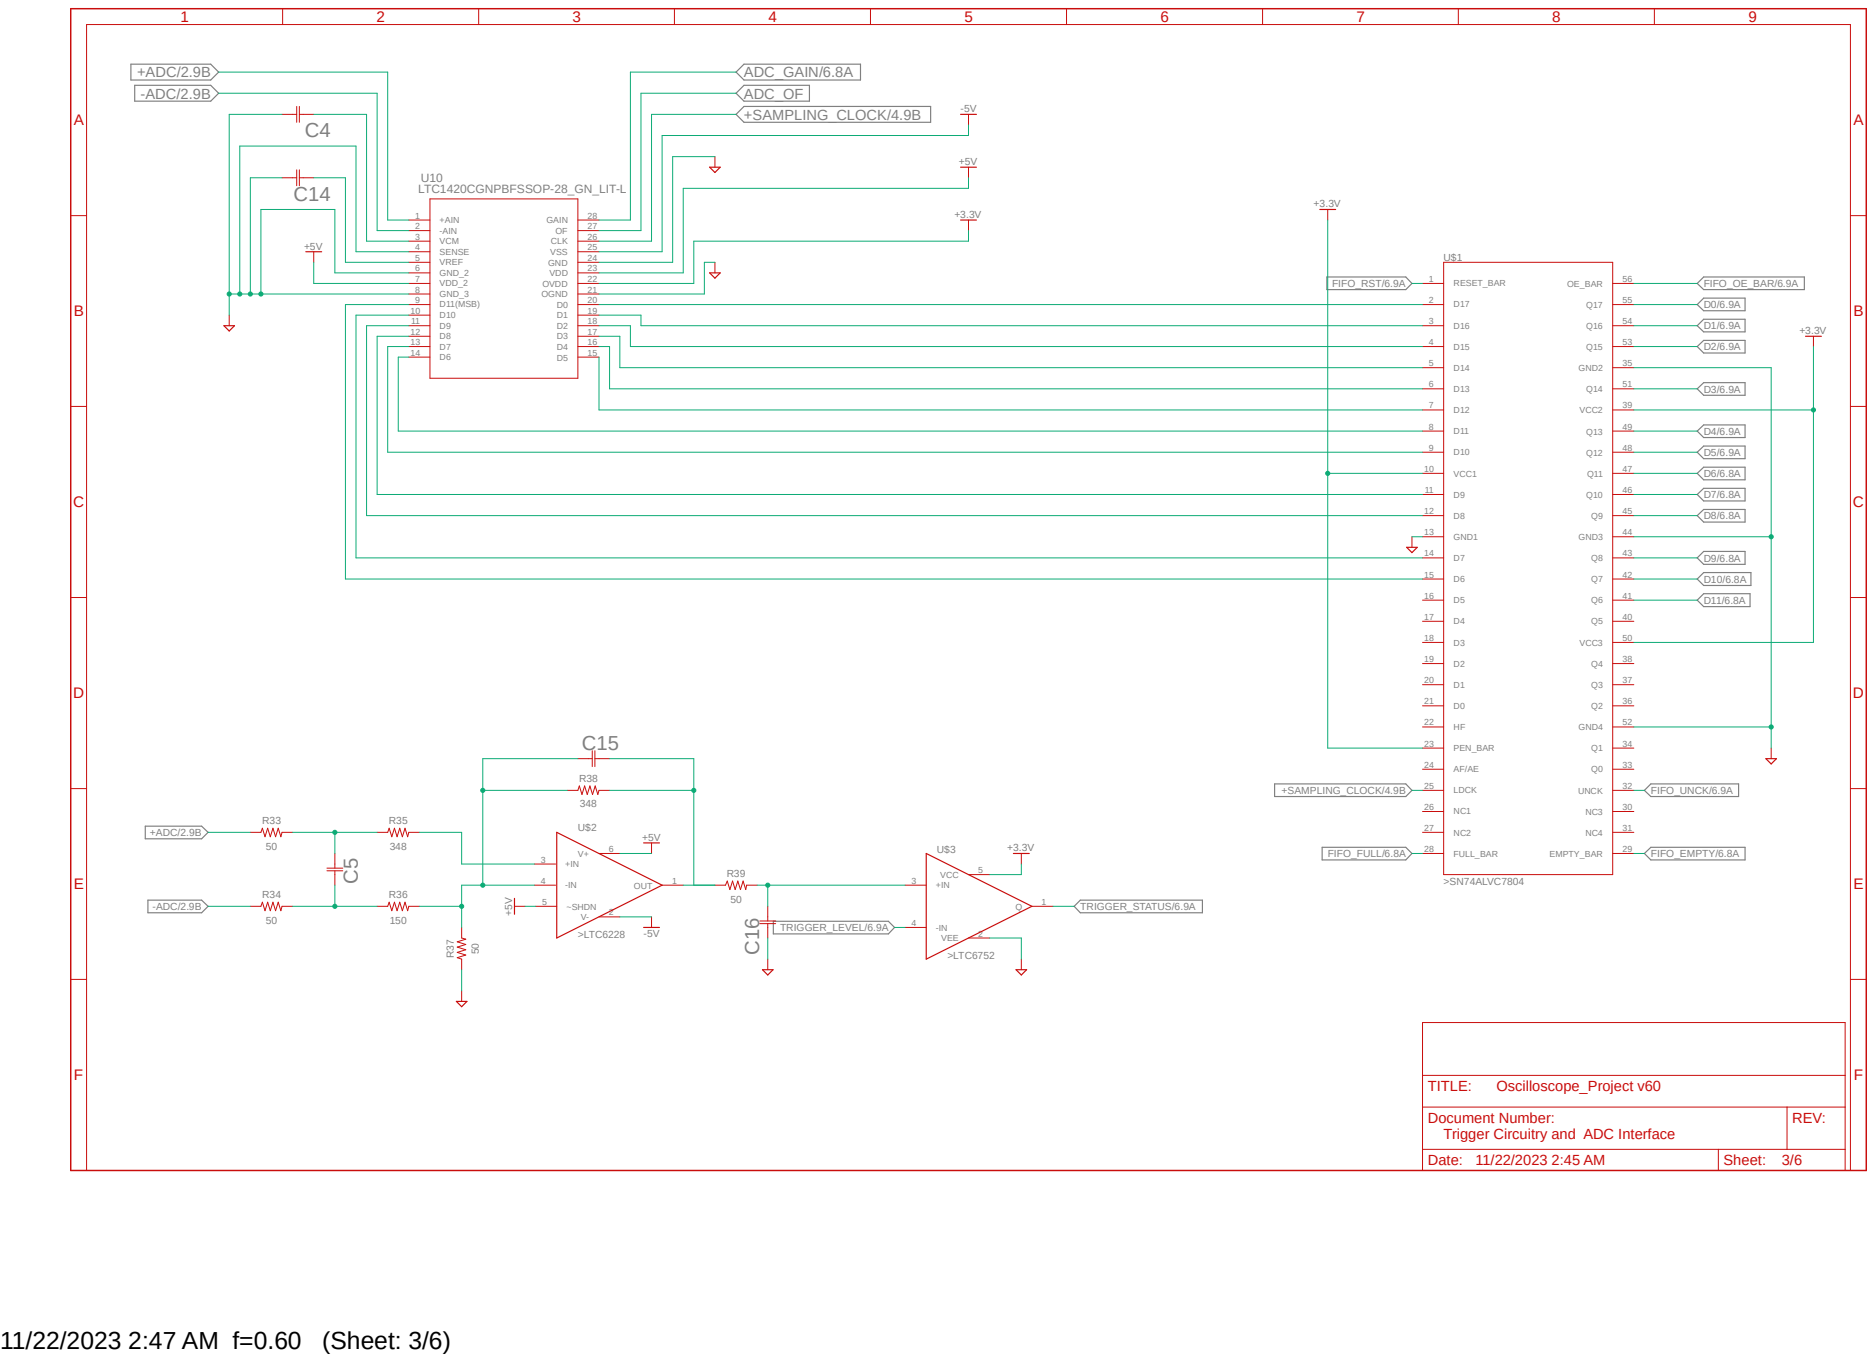
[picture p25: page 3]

Trigger Circuitry and ADC Interface

A

A

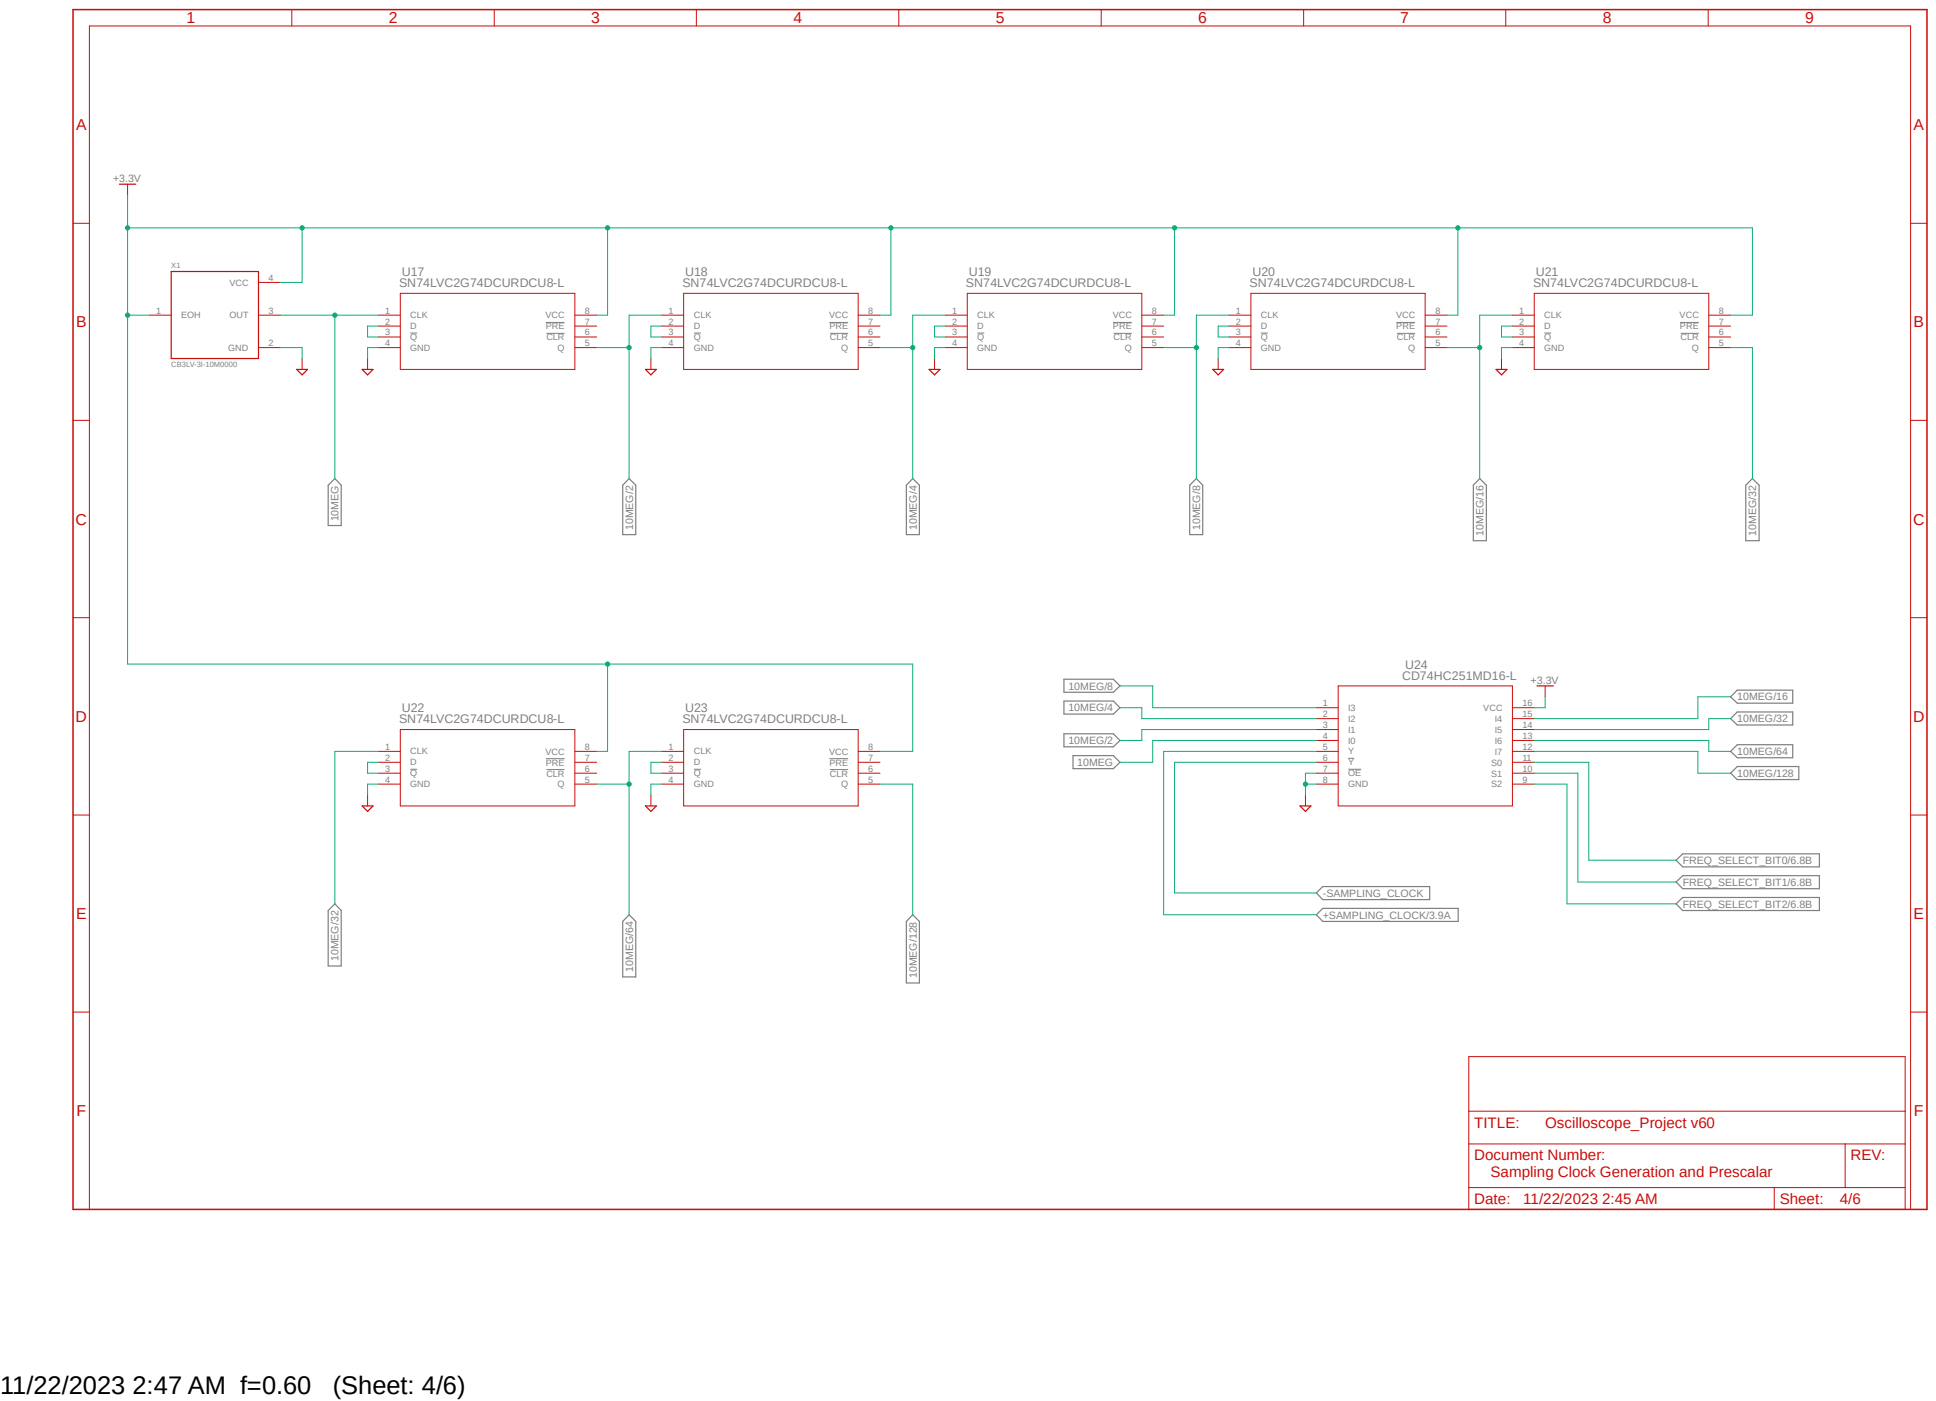
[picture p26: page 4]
11/22/2023 2:47 AM f=0.60 (Sheet: 4/6); SN74LVC2G74DCURDCU8-L; X1EOH 1; OUT; 3 VCC; 4 GND; U17CLK 1; GND 4; 5 CLR; 6 PRE; 7 VCC; U18CLK 1; U19CLK 1; U20CLK 1; U21CLK 1; 8 U22CLK 1; U23CLK 1; GND 8; 15 VCC; 16 ¹⁰MEG; 10MEG ¹⁰MEG/2; 10MEG/2 ¹⁰MEG/4; 10MEG/4; 10MEG/8; 10MEG/16; 10MEG/16 10MEG/32; 10MEG/32 ¹⁰MEG/32 10MEG/64; 10MEG/64 10MEG/128; 10MEG/128 FREQ_SELECT_BIT0/6.8B; FREQ_SELECT_BIT1/6.8B; FREQ_SELECT_BIT2/6.8B; +SAMPLING_CLOCK/3.9A; -SAMPLING_CLOCK; 4/6 Oscilloscope_Project v60 Date: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

Sampling Clock Generation and Prescalar

A

A

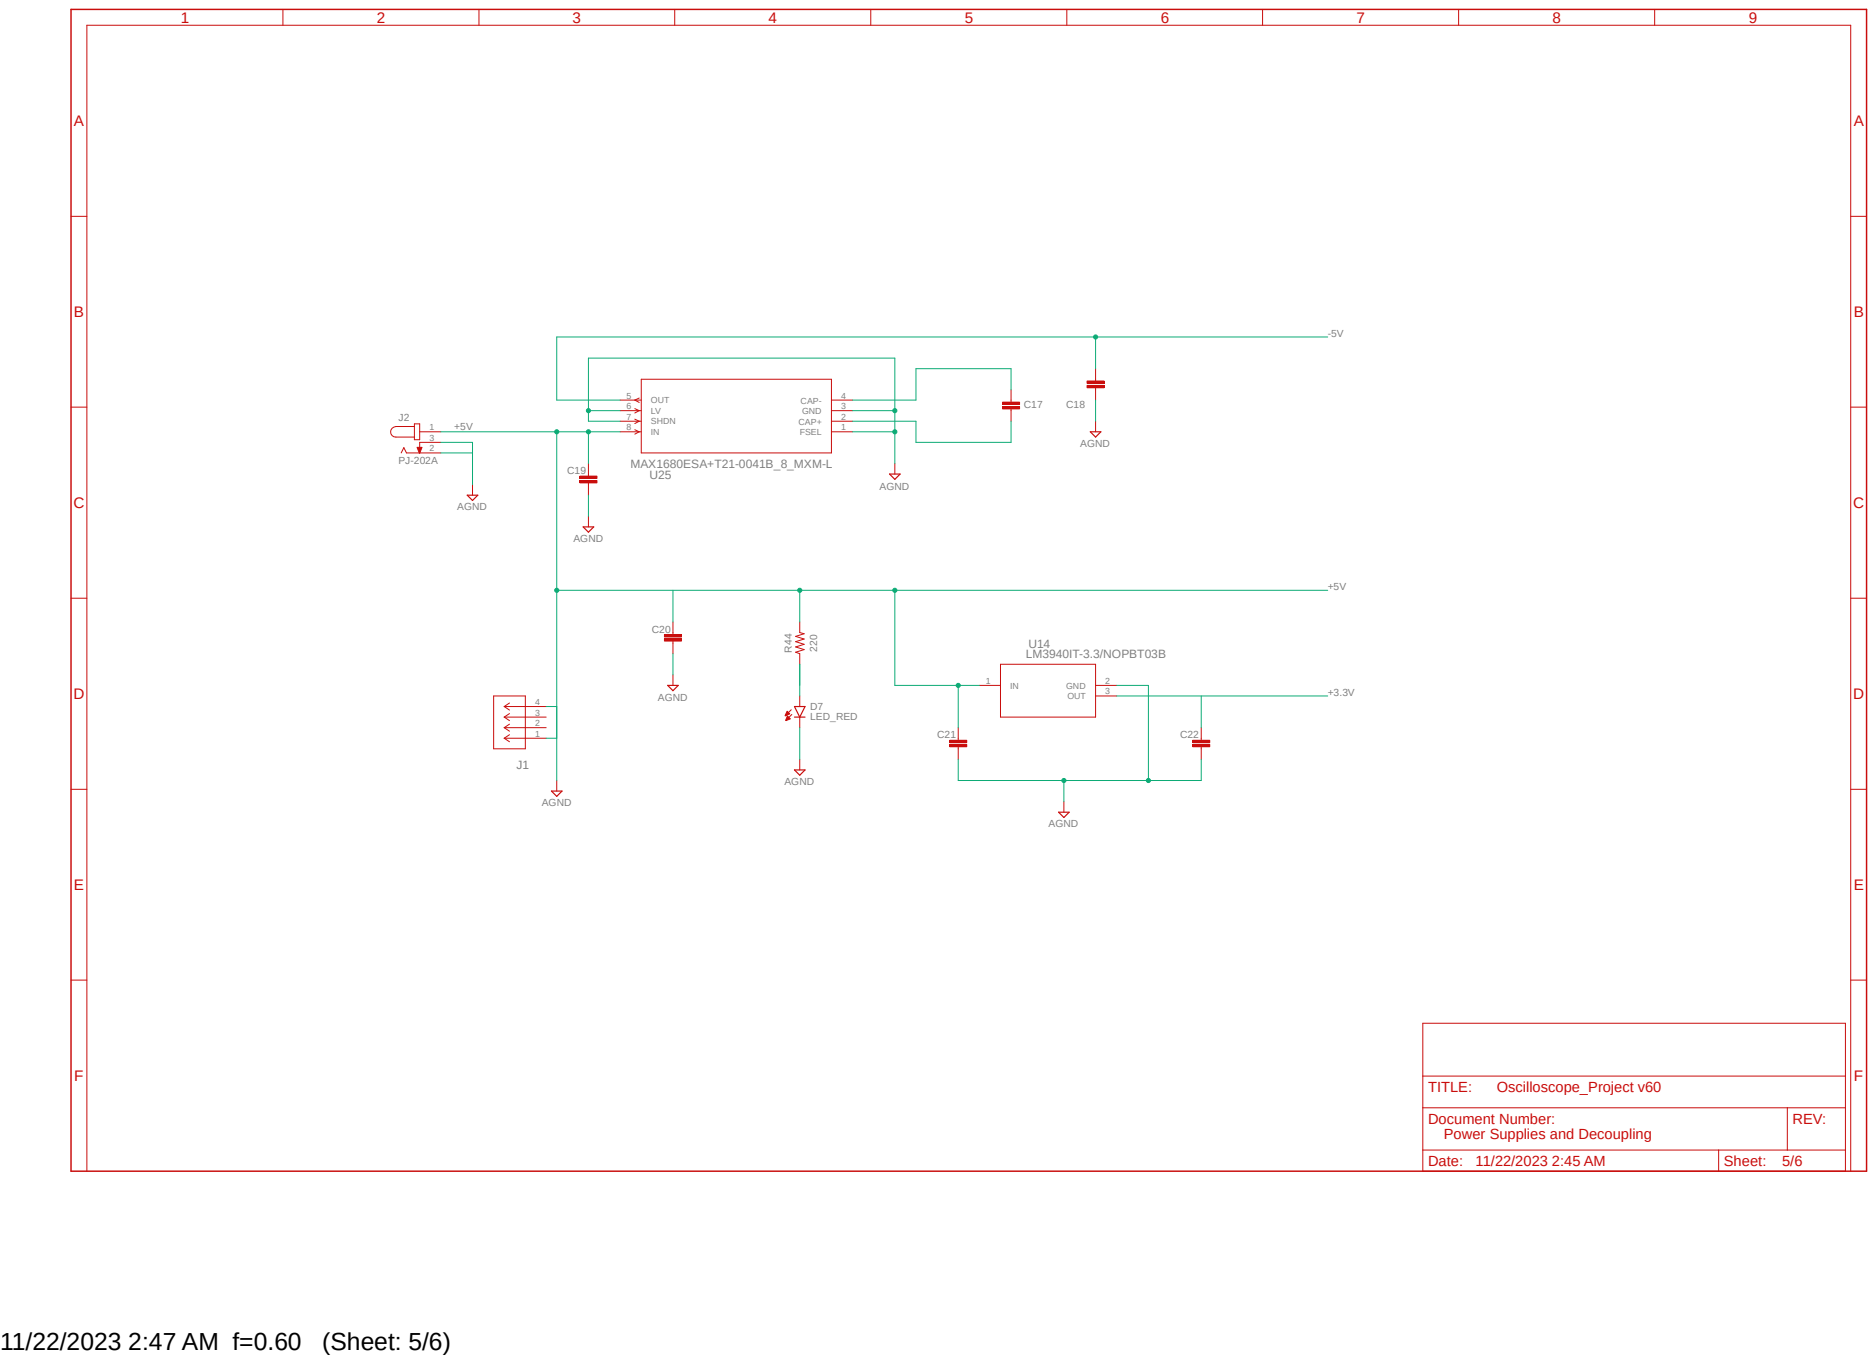
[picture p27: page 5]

Power Supplies and Decoupling

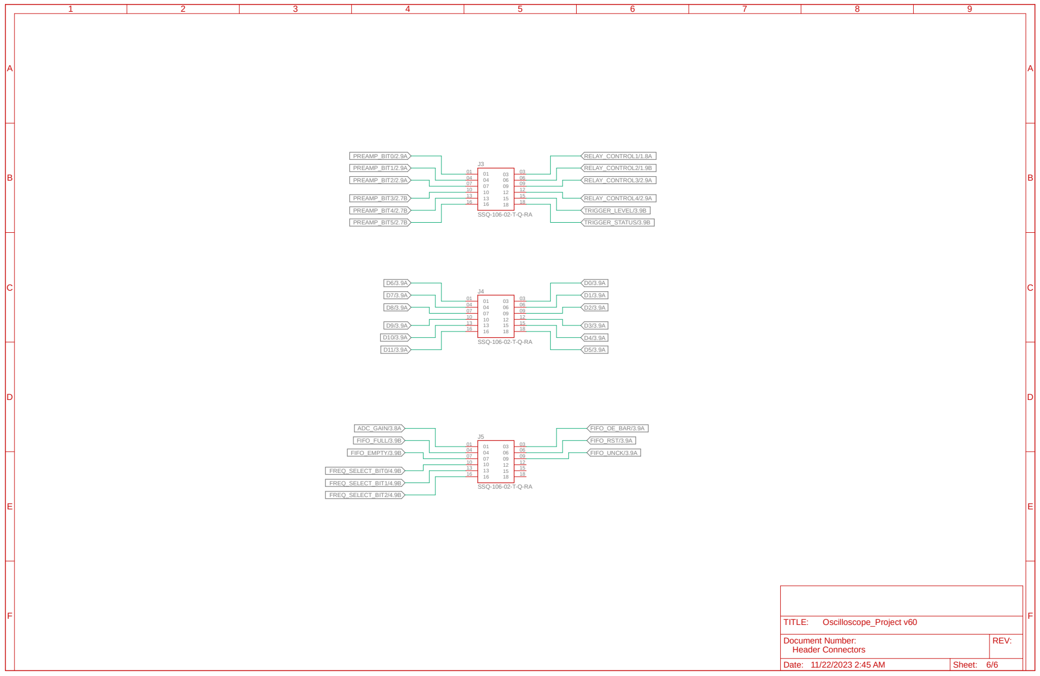
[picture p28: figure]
SSQ-106-02-T-Q-RA; PREAMP_BIT0/2.9A; PREAMP_BIT1/2.9A; PREAMP_BIT2/2.9A; PREAMP_BIT3/2.7B; PREAMP_BIT4/2.7B; PREAMP_BIT5/2.7B; RELAY_CONTROL1/1.8A RELAY_CONTROL2/1.9B RELAY_CONTROL3/2.9A RELAY_CONTROL4/2.9A; TRIGGER_LEVEL/3.9B; ADC_GAIN/3.8A; FREQ_SELECT_BIT1/4.9B; FREQ_SELECT_BIT2/4.9B; FIFO_UNCK/3.9A; FIFO_RST/3.9A; FIFO_OE_BAR/3.9A; FREQ_SELECT_BIT0/4.9B; FIFO_FULL/3.9B

# 11/22/2023 2:46 AM f=0.60 (Sheet: 6/6)

TRIGGER_STATUS/3.9B D0/3.9A D1/3.9A D2/3.9A D3/3.9A D4/3.9A D5/3.9A D6/3.9A D7/3.9A D8/3.9A D9/3.9A D10/3.9A D11/3.9A

FIFO_EMPTY/3.9B | Header Connectors 11/22/2023 2:45 AM | 6/6 Oscilloscope_Project v60 Date: | Sheet: | REV: TITLE: Document Number:

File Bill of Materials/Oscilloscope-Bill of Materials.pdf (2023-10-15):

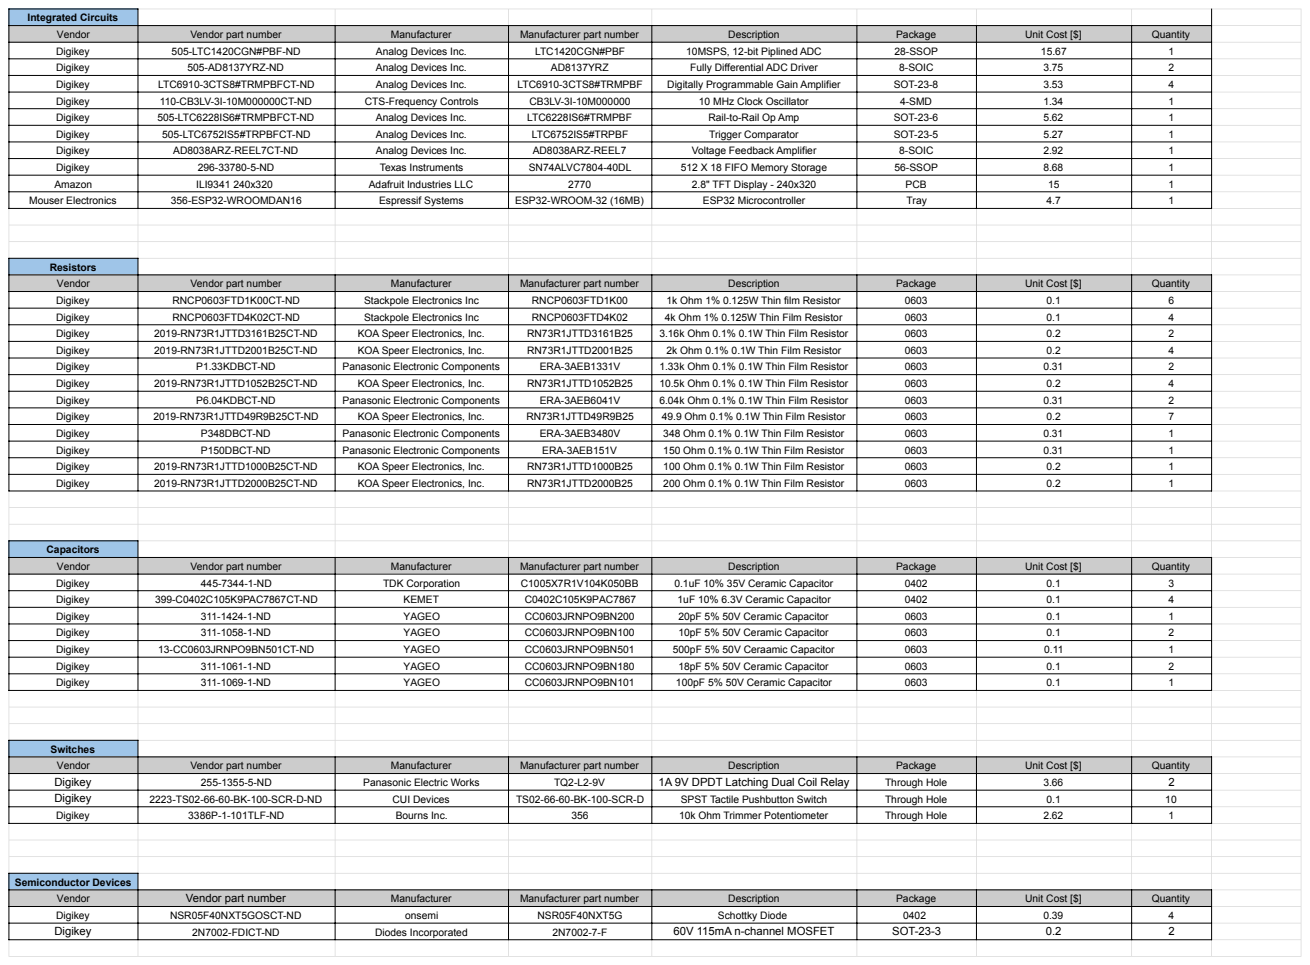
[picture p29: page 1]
Integrated Circuits; Vendor; Vendor part number; Manufacturer; Manufacturer part number; Description; Package; Unit Cost [$]; Quantity Digikey; 505-LTC1420CGN#PBF-ND; Analog Devices Inc.; LTC1420CGN#PBF; 10MSPS, 12-bit Piplined ADC; 28-SSOP; 1 Digikey; 505-AD8137YRZ-ND; AD8137YRZ; Fully Differential ADC Driver; 8-SOIC; 2 Digikey; LTC6910-3CTS8#TRMPBFCT-ND; LTC6910-3CTS8#TRMPBF; Digitally Programmable Gain Amplifier; SOT-23-8; 4 Digikey; CTS-Frequency Controls; 10 MHz Clock Oscillator; 4-SMD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

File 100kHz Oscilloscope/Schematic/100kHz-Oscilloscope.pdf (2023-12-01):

## AD8565AKSZ-REEL7KS_5_ADI-L ⁺³.3V GND

A

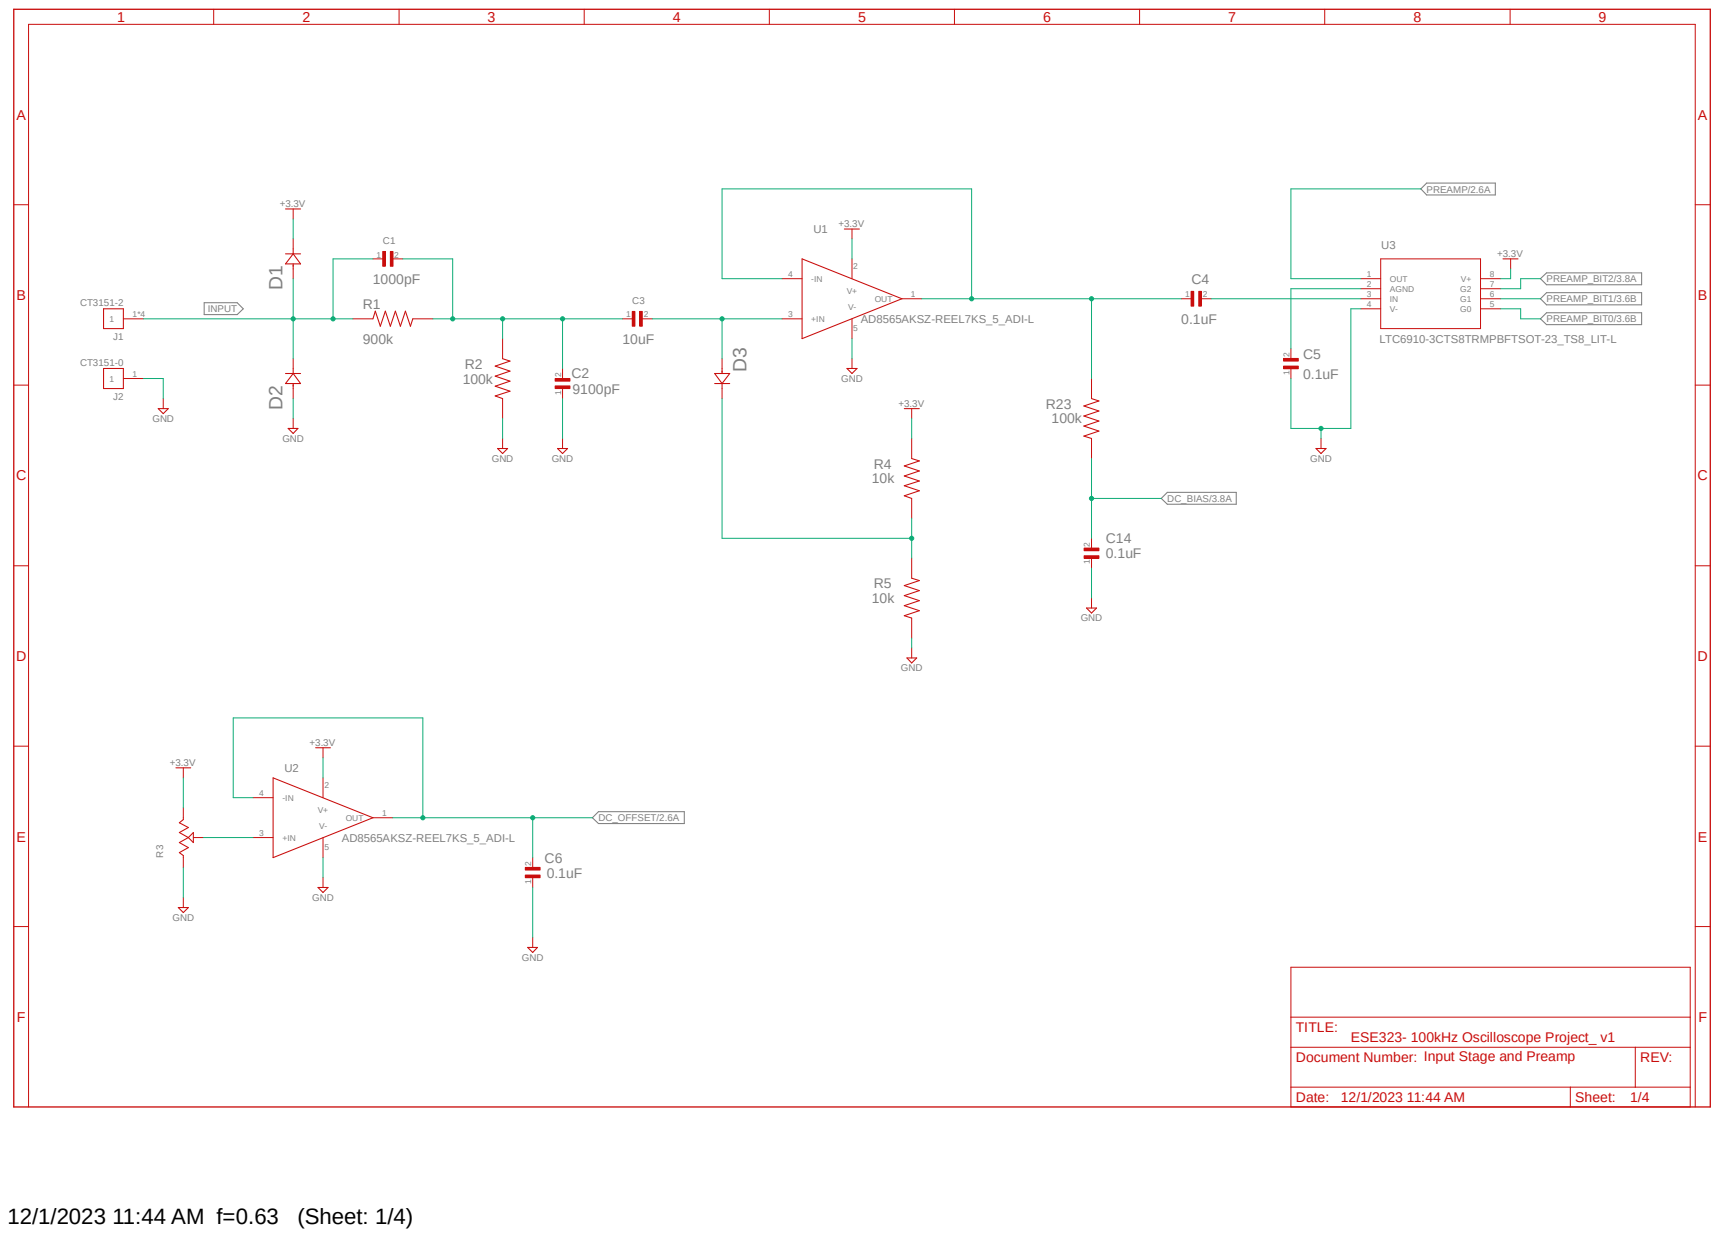
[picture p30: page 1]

Date: Sheet: Input Stage and Preamp | REV: TITLE: Document Number:

10k | 10k

## AD8565AKSZ-REEL7KS_5_ADI-L GND


Date: Sheet: DC Offset and ADC | REV: TITLE: Document Number:

22.1k

1k


Date: Sheet: Bridge, and Power Supply | REV: TITLE: Document Number:

10k

10k

12/1/2023 11:45 AM f=0.63 (Sheet: 4/4); +3.3V GND; TS04-66-50-BK-260-SMT GND; GND; RESET; V/DIV/3.8B; T/DIV/3.8A; TRIGGER_LEVEL/3.8A; X_CURSOR/3.8A; Y_CURSOR/3.8A; DC_OFFSET_SELECT/3.6B; ESE323- 100kHz Oscilloscope Project_ v1

+3.3V GND R²⁴ R²⁵ R²⁶ R²⁷ R²⁸
+3.3V GND

Date: Sheet: Control Knobs and Jumper Wires | REV: TITLE: Document Number:


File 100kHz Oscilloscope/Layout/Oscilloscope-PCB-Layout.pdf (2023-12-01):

R3 R22 USB1

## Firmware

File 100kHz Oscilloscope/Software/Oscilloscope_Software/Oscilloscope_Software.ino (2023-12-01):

#include <Arduino.h>
#include <SPI.h>
#include <TFT_eSPI.h>
#include <freertos/FreeRTOS.h>
#include <freertos/task.h>

// Display dimensions
#define SCREEN_WIDTH 320
#define SCREEN_HEIGHT 240

// MCU Pins
#define TFT_CS 15
#define TFT_DC 2
#define TFT_RST 8

TFT_eSPI tft = TFT_eSPI();
TFT_eSprite xyplane = TFT_eSprite(&tft);  // xy-plane bitmap 
TFT_eSprite waveform = TFT_eSprite(&tft);  // waveform bitmap (buffer to remove flicker) 
TFT_eSprite text_overlay_buffer = TFT_eSprite(&tft);  // virtual canvas for overwriting text without flicker

// ADC data pins 
const int ADC_pins[] = {36, 39, 34, 35, 32, 33, 25, 26};  // [D7 D6 D5 D4 D3 D2 D1 D0]

// Text parameters
const String word_bank[18] = {  // Common strings that will be shown on display
  " V/DIV",      // 0
  " us/DIV",     // 1
  " ms/DIV",     // 2    
  " s/DIV",      // 3
  "Trigger",     // 4
  "(RISING):",   // 5
  "(FALLING):",  // 6
  " Frequency",  // 7
  " Period",     // 8
  " DutyCycle",  // 9
  " Cycle RMS",  // 10
  " Cursors",    // 11
  " X:",          // 12
  " Y:",          // 13
  " DC OFFSET",   // 14
  "Hz",          // 15
  "kHz",         // 16
  "MHz",         // 17
};

const int text_buffer_size = 10;  // number of characters in text overlay buffer
const int font_width = 6;  // width of a character in chosen font (in pixels)
const int font_height = 8;  // height of a character in chosen font (in pixels)

const int text_coordinates[9][2] = {   // [x coordinates][y coordinates]
  {1,1},  // 0 - volts per division coordinates
  {1 + (11*font_width) + (3*font_width), 1},  // 1 - time per division coordinates
  {1 + (11*font_width) + (6*font_width) + (10*font_width), 1},  // 2 - trigger coordinates  
  {260, 70},   // 3 - frequency coordinates
  {260, 100},   // 4 - period coordinates
  {260, 130},  // 5 - duty cycle coordinates
  {260, 160},  // 6 - cycle RMS coordinates
  {260, 30},   // 7 - XY cursor coordinates
  {260, 190}   // 8 - DC offset coordinates
};

const int text_colors[9] = {
  TFT_GREEN,  // 0 - volts per division color
  TFT_BLUE,     // 1 - time per division color  
  TFT_ORANGE,     // 2 - trigger color
  TFT_MAGENTA,    // 3 - frequency color 
  TFT_MAGENTA,    // 4 - period color
  TFT_MAGENTA,    // 5 - duty cycle color
  TFT_MAGENTA,    // 6 - cycle RMS color
  TFT_RED,      // 7 - XY cursors color 
  TFT_GOLD    // 8 - DC offset color
};

char num2string_buffer[5];  // buffer for number to string conversion
String stringbuffer;  // buffer for stroring strings


// graph dimensions (fixed)
const int numDivisionsX = 10;  // number of divisions of x-axis
const int numDivisionsY = 10;  // number of divisions of y-axis

const int graph_width = 250;  // width of x-axis in pixels 
const int graph_height = 200; // height of y-axis in pixels 

const int divisionWidth = (graph_width + 1) / numDivisionsX;  // width of each division in pixels
const int divisionHeight = (graph_height + 1) / numDivisionsY;  // height of each division in pixels

const int gx = 0 + 1;  // bottom left corner of graph; add 1 to close graph (x-coordinate) 
const int gy = 200 + 1;  // bottom left corner of graph; add 1 to close graph (y-coordinate)


// Vertical Scaling parameters
double volts_per_div = 0.1;  // Volts per vertical division
double ylo = volts_per_div*(-(numDivisionsY/2));  // lower bound of y-axis
double yhi = volts_per_div*(numDivisionsY/2);  // upper bound of y-axis
double yinc = (yhi-ylo)*numDivisionsY;   // Resolution of each division of y-axis


// Horizontal Scaling parameters - Horizontal scaling will be done by varying frequency at which data is read from the ADC 
double us_per_div = 100;  // microseconds per horizontal division 
double ms_per_div;  // milliseconds per horizontal division
double s_per_div;  // seconds per horizontal division
double xlo = 0;  // lower bound of x-axis (always start at 0)
double xhi = us_per_div*numDivisionsX;  // upper bound of x-axis
double xinc = (xhi-xlo)/numDivisionsX;   // Resolution of each division of x-axis


// Plotting parameters
double trigger_level = 0.27; // tigger voltage
uint8_t ADCsamplebuffer[2000]; // samples taken from AD 
double ox , oy;  // most recently plotted xy corrdinates
double x, y;  // xy coordinates to be plotted
boolean graph_reset = true;  // flag to reset starting position of graph when plotting
int x_cursor = 1;
int y_cursor = 1;
// dc offset triangle icon coordinates
const int trig_symbolx1 = 8; int trig_symboly1 = 120;
int trig_symbolx2 = 0; int trig_symboly2 = 124;  
int trig_symbolx3 = 0; int trig_symboly3 = 116;

// Measurement and display scalaing parameters
double frequency = 100;
double period = 10;
double duty_cycle = 50;
double cycle_rms = 3.54;
double dc_offset = 0;

// Function Declarations
void initializeText();
void Graph(TFT_eSprite &d, double x, double y, double gx, double gy, double w, double h, double xlo, double xhi, double xinc, double ylo, double yhi, double yinc, unsigned int gcolor, unsigned int acolor, unsigned int pcolor, unsigned int bcolor, boolean &redraw);
void movetrigIconDown(int value);
void movetrigIconUp(int value);
void changeCyclerms(double value);
void changeDutycycle(double value);
void changeFreq(double value, String unit); 
void changePeriod(double value, String unit); 
void changeVoltsperDiv(double value);
void changeTimeperDiv(double value, String unit);
void changeTriggerLevel(double value);

void poll_ADC_Task(void *parameter);

void setup() {
  Serial.begin(9600);

  tft.init();  
  tft.setRotation(1); // set display orientation
  tft.setTextWrap(false); // Disable text wrap
  tft.fillScreen(TFT_BLACK);  
  tft.setTextSize(1);

  // Configure GPIO pins
  for (int i = 0; i < sizeof(ADC_MSB_nibble) / sizeof(ADC_MSB_nibble[0]); i++) {
    pinMode(ADC_MSB_nibble[i], INPUT);
  }

  for (int i = 0; i < sizeof(ADC_LSB_nibble) / sizeof(ADC_LSB_nibble[0]); i++) {
    pinMode(ADC_LSB_nibble[i], INPUT);
  }

// Task to poll output from ADC
  xTaskCreatePinnedToCore(
    poll_ADC_Task,       // Function to implement the task
    "poll_ADC_Task",     // Name of the task
    10000,              // Stack size (bytes)
    NULL,               // Task parameters
    1,                  // Priority (1 is default)
    NULL,               // Task handle
    0                   // Core to run the task on (0 or 1)
  );
// Task to plot waveform on display
  xTaskCreatePinnedToCore(
    plot_data_Task,       // Function to implement the task
    "plot_data_Task",     // Name of the task
    10000,              // Stack size (bytes)
    NULL,               // Task parameters
    1,                  // Priority (1 is default)
    NULL,               // Task handle
    0                   // Core to run the task on (0 or 1)
  );



  // test signal for plotting (not part of final design)
  for(int i = 0; i < 250; i++)   {
      ADCsamplebuffer[i] = 5*sin((5*i*(6.5/250)));
  }

  waveform.createSprite(graph_width + 1, graph_height + 1); 
  // Clear the canvas and draw the graph lines
  xyplane.createSprite(graph_width + 1, graph_height + 1);  // XY-plane is 250x200 pixels
  xyplane.fillSprite(TFT_BLACK);  // XY-plane has black background

  // draw x-axis divisions
  for (int x = 0; x < xyplane.width(); x += divisionWidth) {
    xyplane.drawFastVLine(x, 0, xyplane.height(), TFT_LIGHTGREY);
  }
  // draw y-axis divisions
  for (int y = 0; y < xyplane.height(); y += divisionHeight) {
    xyplane.drawFastHLine(0, y, xyplane.width(), TFT_LIGHTGREY);
  }
  
  text_overlay_buffer.createSprite(text_buffer_size*font_width, font_height);  // sprite is large enough for a set number of characters
  initializeText();
  tft.fillTriangle(trig_symbolx1, trig_symboly1, trig_symbolx2, trig_symboly2, trig_symbolx3, trig_symboly3, text_colors[8]);

  movetrigIconUp(double(dc_offset/volts_per_div)*(graph_height/numDivisionsY));

  // set ADC parameters:
  analogReadResolution(12);  // Set ADC resolution to 12 bits (0-4095)
  analogSetAttenuation(ADC_0db);  // Set ADC attenuation to DEFAULT (0-1.1V range)
}


void poll_ADC_Task (void *paramter) { // Store 2000 samples from ADC in memory
  (void) parameter; // Unused parameter
  setCpuFrequencyMhz(240);  // Overclock for maximum GPIO sample rate
  for (int i = 0; i < 1999; i++) {
    ADCsamplebuffer[i] = 0;
    for (int j = 0; j < sizeof(ADC_pins) / sizeof(ADC_pins[0]); j++) {
      ADCsamplebuffer[i] = |= (digitalRead(ADC_pins[j] << j));
    }
  }
  vTaskDelay(1); // Small delay to avoid consuming too much CPU time
}


void plot_data_Task (void *paramter) { // Plot data on LCD display

  // Display the canvas on the ILI9341 display
  xyplane.pushToSprite(&waveform,0,0);

  // Map binary values to 0-3.3V range
  for (int i = 0; i < 1999; i++) {    
    ADCsamplebuffer[i] = (double)ADCsamplebuffer[i] / 255 * 3.3; 
  }

  // Poll potentiometer knobs to figure out scaling parameters
  /*  ......
      ......
      ......
  */

  // Figure out which samples to plot....Decimate sequence for higher time/DIV
  /*  ......
      ......
      ......
  */
  
  // Plot samples with graph function...
  /*  ......
      ......
      ......
  */

  waveform.drawFastHLine(0, y_cursor, waveform.width(), TFT_RED);   // Draw Y-cursor
  waveform.drawFastVLine(x_cursor , 0, waveform.height(), TFT_RED);   // Draw X-cursor
  waveform.pushSprite(10,20);
  vTaskDelay(1); // Small delay to avoid consuming too much CPU time
}

void loop() {
  // Display the canvas on the ILI9341 display
  xyplane.pushToSprite(&waveform,0,0);

  while (1) {
    int adc_input = analogRead(36); // read anaolg input from GPIO 36
    double mappedValue = (double)adc_input / 4095.0 * 1.1; // Convert to voltage (0-1.1V)

    Serial.println(mappedValue, 4);

//    if (mappedValue >= (trigger_level - 0.1) && mappedValue <= (trigger_level + 0.1)) {
      for(int i = 0; i < 250; i++) {
        adc_input = analogRead(36); // read anaolg input from GPIO 36
        mappedValue = (double)adc_input / 4095.0 * 1.1; // Convert to voltage (0-1.1V)
        ADCsamplebuffer[i] = mappedValue;

    }
    delay(1000);
        break;
  }

  for (int i = 249; i >= 0; i--) {
    Graph(waveform, i*(xhi/250), (dc_offset + ADCsamplebuffer[i]), gx, gy, graph_width, graph_height, xlo, xhi, xinc, ylo, yhi, yinc, TFT_LIGHTGREY, TFT_RED, TFT_YELLOW, TFT_BLACK, graph_reset);
  }

  waveform.drawFastHLine(0, y_cursor, waveform.width(), TFT_RED);
  waveform.drawFastVLine(x_cursor , 0, waveform.height(), TFT_RED);

  waveform.pushSprite(10,20);
  graph_reset = true;
}




void Graph(TFT_eSprite &d, double x, double y, double gx, double gy, double w, double h, double xlo, double xhi, double xinc, double ylo, double yhi, double yinc, unsigned int gcolor, unsigned int acolor, unsigned int pcolor, unsigned int bcolor, boolean &redraw) {

  double temp;

  if (redraw == true) {
    redraw = false;
    // initialize first points on display
    ox = (x - xlo) * (w) / (xhi - xlo) + gx;
    oy =  (y - ylo) * (-h) / (yhi - ylo) + gy;
  }
  else {
    // compute transform
    x =  (x - xlo) * (w) / (xhi - xlo) + gx;
    y =  (y - ylo) * (-h) / (yhi - ylo) + gy;
    d.drawLine(ox, oy, x, y, pcolor); 
    d.drawLine(ox, oy + 1, x, y + 1, pcolor);
    d.drawLine(ox, oy - 1, x, y - 1, pcolor); 
    ox = x;
    oy = y;
  }
}

void changeVoltsperDiv(double value) {
  volts_per_div = value;
  ylo = volts_per_div*(-(numDivisionsY/2));  
  yhi = volts_per_div*(numDivisionsY/2);  
  yinc = (yhi-ylo)*numDivisionsY;   
  
  tft.fillRect(text_coordinates[0][0], text_coordinates[0][1], 11*font_width, font_height, TFT_BLACK);
  tft.setTextColor(text_colors[0]);
  dtostrf(volts_per_div, 2, 2, num2string_buffer);
  tft.setCursor(text_coordinates[0][0], text_coordinates[0][1]);
  tft.print(num2string_buffer);tft.print(word_bank[0]);
}
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
